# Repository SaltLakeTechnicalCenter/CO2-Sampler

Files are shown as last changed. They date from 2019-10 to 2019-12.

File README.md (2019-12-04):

# Introduction
This device uses an infrared gas sensor from [Dynament](https://www.dynament.com/gas-types/carbon-dioxide/) to monitor the concentration of carbon dioxide in the air.  When threshold conditions are met an [Entech Micro-QT valve](https://www.entechinst.com/product-category/micro-qt-valves/) on an evacuated chamber is open allowing a sample of the air to be captured.  This is accomplished by pressing a tube into the valve with a SG90 servo motor connected to a cam.  A [LilyGO TTGO T2 development board](https://www.amazon.com/TTGO-T2-Bluetooth-Development-Module/dp/B07B6MS253) communicates with the sensor (via [RS232](https://www.dynament.com/_webedit/uploaded-files/All%20Files/SIL%20Data/tds0045_1.44.pdf)) and logs data to a microSD card.  A simple user interface is accomplished with the onboard button and OLED display. More advanced features will be accessable through an Android device paired to the onboard bluetooth.

# Pinout
| GPIO |  Device |            Notes           |
|------|---------|----------------------------|
|   0  |         | outputs PWM signal at boot |
|   1  |  Serial |      serial monitor TX     |
|   2  |   RFID  |         Dynament RX        |
|   3  |  Serial |      serial monitor RX     |
|   4  |   OLED  |             RST            |
|   5  | SD card |             CS             |
| 6    | SPI     | SPI flash                  |
| 7    | SPI     | SPI flash                  |
| 8    | SPI     | SPI flash                  |
| 9    | SPI     | SPI flash                  |
| 10   | SPI     | SPI flash                  |
| 11   | SPI     | SPI flash                  |
| 12   |         | boot fail if pulled high   |
| 13   | OLED    | MOSI/SDA                   |
| 14   | OLED    | SCLK/SCL                   |
| 15   | OLED    | CS                         |
| 16   | OLED    | DC                         |
| 17   | RFID    | Dynament TX                |
| 18   | SD card | CLK                        |
| 19   | SD card | DO MISO                    |
| 21   | BMP180  | SDA                        |
| 22   | BMP180  | SCL                        |
| 23   | SD card | CMP/MOSI                   |
| 25   |         |                            |
| 26   |         |                            |
| 27   | Buzzer  | Buzzer                     |
| 32   | Servo   | Servo                      |
| 33   |         |                            |
| 34   | RFID    | Analog                     |
| 35   | Battery | Battery                    |
| 36   | Button  | Button                     |
| 39   |         | Inaccessible               |

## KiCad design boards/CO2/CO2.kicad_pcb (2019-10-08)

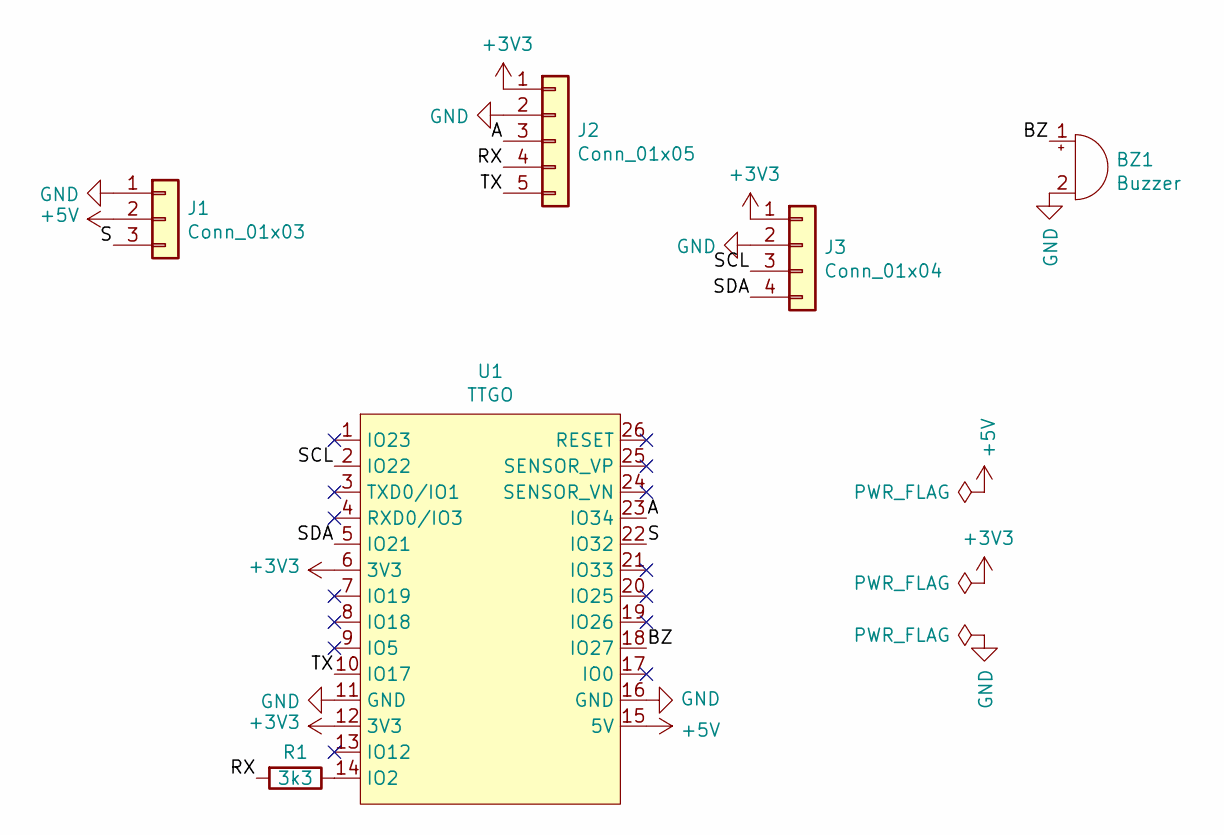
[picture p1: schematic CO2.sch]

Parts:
BZ1: Buzzer; Buzzer_12x9.5RM7.6
J1: Conn_01x03; PinHeader_1x03_P2.54mm_Horizontal
J2: Conn_01x05; JST_XH_S5B-XH-A_1x05_P2.50mm_Horizontal
J3: Conn_01x04; PinHeader_1x04_P2.54mm_Vertical
R1: 3k3; R_Axial_DIN0204_L3.6mm_D1.6mm_P7.62mm_Horizontal
U1: TTGO

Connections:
+3V3: J2.1, J3.1, U1.6 (3V3), U1.12 (3V3)
+5V: J1.2, U1.15 (5V)
/A: J2.3, U1.23 (IO34)
/BZ: BZ1.1 (-), U1.18 (IO27)
/RX: J2.4, R1.2
/S: J1.3, U1.22 (IO32)
/SCL: J3.3, U1.2 (IO22)
/SDA: J3.4, U1.5 (IO21)
/TX: J2.5, U1.10 (IO17)
GND: BZ1.2 (+), J1.1, J2.2, J3.2, U1.11 (GND), U1.16 (GND)
unnamed: R1.1, U1.14 (IO2)

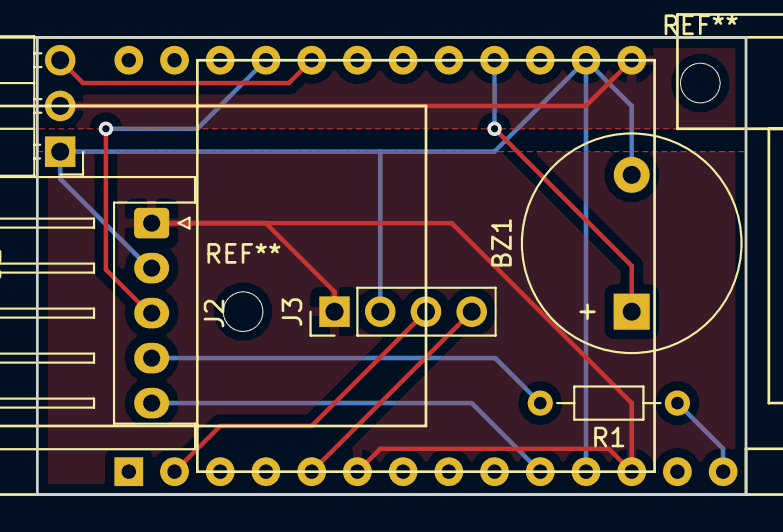
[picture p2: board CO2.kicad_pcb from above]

Board: 2 copper layers, 39.4 x 25.4 mm, 6 parts (0 on the bottom side), 11 nets.

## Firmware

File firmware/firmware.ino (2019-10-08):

#define BUZZER 27
#define BATTERY 35
#define BUTTON 36

#include <SPI.h>
#include "SSD_13XX.h" //https://github.com/sumotoy/SSD_13XX
#define __CS    15  
#define __DC    16 
#define __RST   4
//define __mosi 23
//define __sclk 18
SSD_13XX tft = SSD_13XX(__CS, __DC, __RST);

#include "FS.h"
#include "SD.h"
#include "SPI.h"
char cstr[16];

#include <HardwareSerial.h>
HardwareSerial Dynament(2);
#define DynamentRX 17
#define DynamentTX 2
#define DynamentAnalogPIN 34
#define DynamentBAUD 38400
#define __CS    15  
#define __DC    16 
#define __RST   4
//define __mosi 23
//define __sclk 18

#include <Wire.h>
#include <Adafruit_BMP085.h>
Adafruit_BMP085 bmp;

#include <Servo.h>
static const int servoPin = 32;
Servo servo1;

struct liveDataSimple_t{
  union { byte b[2]; uint16_t i; } Version;
  union { byte b[2]; uint16_t i; } statusFlags;
  union { byte b[4]; float f; } gasReading;
};

struct liveData_t{
  union { byte b[2]; uint16_t i; } Version;
  union { byte b[2]; uint16_t i; } statusFlags;
  union { byte b[4]; float f; } gasReading;
  union { byte b[4]; float f; } temperature;
  union { byte b[2]; uint16_t i; } Det;
  union { byte b[2]; uint16_t i; } Ref;
  union { byte b[4]; float f; } Fa;
};

unsigned long currentMillis = millis(), previousMillis = 0, sampleTime = 1000; // milliseconds
float gasReading;
int analogValue;
String serialNumber = "ERROR!";
boolean doWriteSD = false;
liveData_t liveData;

void setup() {
  pinMode(BUZZER, OUTPUT);
  digitalWrite(BUZZER, LOW);
  pinMode(BUTTON, INPUT);
  pinMode(DynamentAnalogPIN, INPUT);
  Serial.begin(115200);
  Serial.println("Hello World");
  tft.begin();
  tft.println("Hello World");
  initSD();
  writeFile(SD, "/datalog.txt", "Time,Gas Reading,Temperature,Detector,Reference,Absorbance,Analog,Pressure,Temperature\n");
  Dynament.begin(DynamentBAUD, SERIAL_8N1, DynamentRX, DynamentTX);
  getSerialNumber();
  if (!bmp.begin()) {
    Serial.println("Could not find a valid BMP085 sensor, check wiring!");
    while (1) {}
  }
  servo1.attach(servoPin);
  servo1.write(0);
}

void loop() {
  currentMillis = millis();
  if(currentMillis - previousMillis > sampleTime) {
    previousMillis = currentMillis;
    readSensor();
    if (doWriteSD) writeSD();
  }
  if (!digitalRead(BUTTON)) buttonPress();
}

void buttonPress() {
  itoa(millis(), cstr, 10);
  digitalWrite(BUZZER, HIGH);
  if (doWriteSD) {
    doWriteSD = false;
    appendFile(SD, "/datalog.txt", "Stopped logging data at ");
  }
  else {
    doWriteSD = true;
    appendFile(SD, "/datalog.txt", "Started logging data at ");
  }
  appendFile(SD, "/datalog.txt", cstr);\
  appendFile(SD, "/datalog.txt", " milliseconds.\n");
  tft.clearScreen();
  tft.fillScreen(RED);
  tft.println("Hello World!");
  servo1.write(180);
  delay(1000);
  digitalWrite(BUZZER, LOW);
  servo1.write(0);
  tft.clearScreen();
}

void writeSD() {
  //itoa(millis(), cstr, 10);
  //appendFile(SD, "/datalog.txt", "Writing to SD card at ");
  //appendFile(SD, "/datalog.txt", cstr);\
  //appendFile(SD, "/datalog.txt", " milliseconds.\n");
  static char buffer[50];
  sprintf (buffer, "%5lu,%1.3f,%1.3f,%4lu,%4lu,%1.5f,%4lu,%6lu,%1.3f\n",currentMillis/1000,liveData.gasReading.f,liveData.temperature.f,liveData.Det.i,liveData.Ref.i,liveData.Fa.f,analogValue,bmp.readPressure(),bmp.readTemperature());
  appendFile(SD, "/datalog.txt", buffer);
}

void readSensor() {
  liveData = getLiveData();
  analogValue = analogRead(DynamentAnalogPIN);
  tft.clearScreen();
  tft.print("Serial Number: "); tft.println(serialNumber);
  char buf[21];
  sprintf(buf,"Time: %02d:%02d:%02d",(currentMillis/1000/60/60),(currentMillis/1000/60)%60,(currentMillis/1000)%60);
  tft.println(buf);
  tft.print("Gas: "); tft.println(liveData.gasReading.f);
  tft.print("Temp: "); tft.print(liveData.temperature.f); tft.println(" °C");
//  tft.print("Detector: "); tft.println(liveData.Det.i);
//  tft.print("Reference: "); tft.println(liveData.Ref.i);
//  tft.print("Absorbance: "); tft.println(liveData.Fa.f);
  tft.print("Analog: "); tft.println(analogValue);
  tft.print("Pres = "); tft.print(bmp.readPressure()); tft.println(" Pa.");
  tft.print("Temp = "); tft.print(bmp.readTemperature()); tft.println(" °C.");
}

void readSensorOLD() {
  gasReading = getGasReading();
  analogValue = analogRead(DynamentAnalogPIN);
  tft.clearScreen();
  tft.print("Serial Number: "); tft.println(serialNumber);
  tft.print("Time: "); tft.println(currentMillis/1000);
  tft.print("Gas Reading: "); tft.println(gasReading);
  tft.print("Analog Reading: "); tft.println(analogValue);
}
